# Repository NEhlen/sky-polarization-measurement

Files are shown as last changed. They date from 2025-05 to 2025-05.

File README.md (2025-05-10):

# Sky Polarization Measurement

## Idea
Use four photodiodes with linear polarization filters attached on top with 0°, 45°, 90°, 135° rotation respectively.

From the relative intensities of the measured illumination it is then possible to determine the polarization direction and strength of a light source.

Adding a long tube as a "collimator" along the surface normal of the photodiodes will enable to sample small patches of the sky.

Combining this setup with a 9dof sensor-fusion IMU recording the alt-az and rotation of the tube it is then possible to sway the tube around and continuously record polarization strength/direction to sample the whole sky.

This can be compared to the [Rayleigh sky polarization model](https://en.wikipedia.org/wiki/Rayleigh_sky_model).

## Description
This project uses an ESP32 microcontroller and four BPW34 photodiodes to measure the polarization of the sky. The ESP32 runs a local Wi-Fi access point and serves a JSON API of real-time light intensity values. The analog signals are read using a transimpedance amplifier (TIA) configuration with LM324 op-amps.

## Hardware
### Components
* Espressif ESP32 development board (1x)
* BPW 34 photodiodes (OSRAM) (4x)
* LM 324 Transimpedance amplifier
* GY-9250 9Axis IMU / Adafruit ICM-20948 9-DoF
* Feedback resistors (100&nbsp;kΩ - 1&nbsp;MΩ) (4x)

### Wiring

#### BPW34 / LM324
Each BPW34 photodiode is reverse-biased in a TIA circuit:

* Photodiode anode → GND

* Photodiode cathode → inverting input of LM324

* LM324 non-inverting input → GND

* Feedback resistor between op-amp output and inverting input

* LM324 output → ESP32 analog input (GPIO32, 33, 34, 35)

The LM324 has four op-amps in one package, so one IC is sufficient for all four photodiodes. This is a valid and efficient setup, provided each channel is correctly biased and isolated.

LM324 is powered with 5V (from USB or VIN pin of ESP32).

#### ICM-20948

The ICM-20948 is a 9-axis IMU that combines a 3-axis gyroscope, a 3-axis accelerometer, and a 3-axis magnetometer. Connect it to the ESP32 using the I²C interface as follows:

* **ICM-20948 VCC** → **ESP32 3.3V**
* **ICM-20948 GND** → **ESP32 GND**
* **ICM-20948 SDA** → **ESP32 GPIO21**
* **ICM-20948 SCL** → **ESP32 GPIO22**

Ensure pull-up resistors (typically 4.7kΩ) are present on the SDA and SCL lines if not already included on the breakout board.

#### Breadboard Sketch

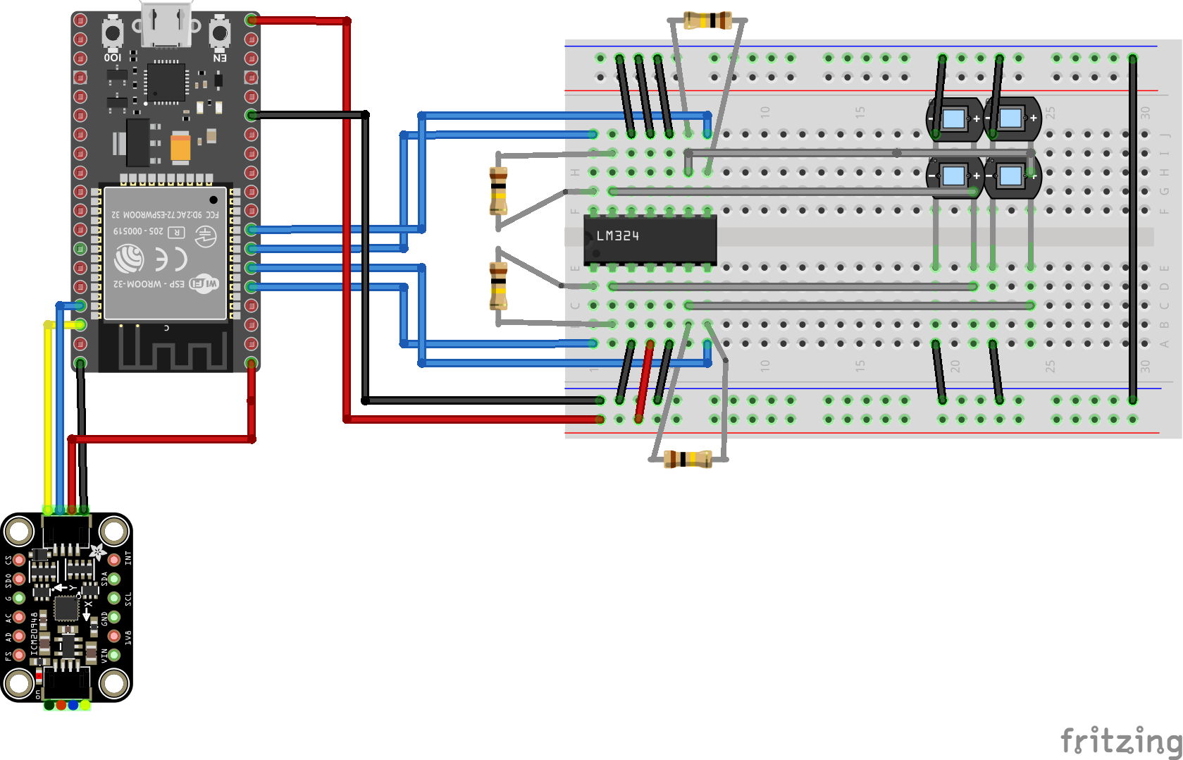
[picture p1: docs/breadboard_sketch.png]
Diode Readout Breadboard Sketch


### Polarizer Setup

Mount the polarizers in front of the photodiodes at 0°, 45°, 90°, and 135° to analyze linear polarization components.

#### BPW 34
The photodiodes are encased in a plastic housing, they are sensitive to vis and near-ir light. The cathode side is marked by a small protrusion on its pin.
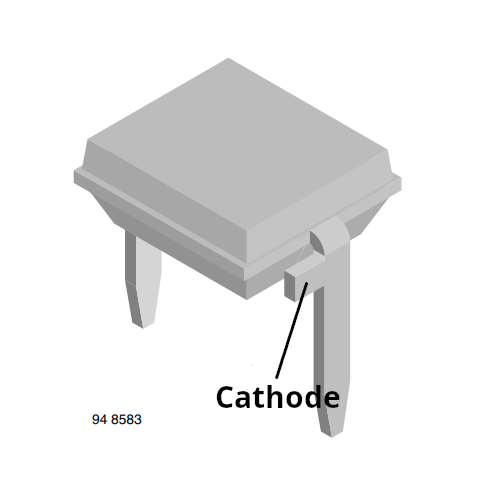
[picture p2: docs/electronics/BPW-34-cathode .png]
Cathode marker


In broad daylight, a voltage of about $0.5-1\,\mathrm{V}$ is produced by a single photodiode. To increase sensitivity and reaction time, the Photodiodes are used in **photoconductive mode** in combination with an LM 324 op-amp rather than **photovoltaic mode** (zero-bias).

#### ICM-20948

The ICM-20948 requires proper initialization in the firmware to read sensor data. Libraries such as [Adafruit's ICM-20948 library](https://github.com/adafruit/Adafruit_ICM20948) can simplify communication and data processing. However, the Adafruit ICM-20948 library **does not give low level access to the digital motion processor (DMP)** on the ICM-20948.
Instead, use the [SparkFun ICM-20948 Arduino Library](https://github.com/sparkfun/SparkFun_ICM-20948_ArduinoLibrary).

The DMP offers a `INV_ICM20948_SENSOR_ORIENTATION` mode that enables access to the 32-bit 9-axis quaternion + heading accuracy without needing to do any additional sensor fusion on the firmware side. From the quaternion, the Euler angles for `yaw`, `tilt` and `roll` can be calculated in the usual manner. This gives alt-az and roll.

## Firmware (ESP32)
The ESP32 sets up a local Wi-Fi Access Point and serves light intensity values as well as alt-az-rot of the ICM-20948 via HTTP at http://192.168.4.1/.

See the firmware at `scripts/esp32/esp32-photodiode-readout-server.ino`

### Serial Plotting
The firmware also prints raw sensor values over serial (space-separated) so you can use the Arduino Serial Plotter for real-time visualization.
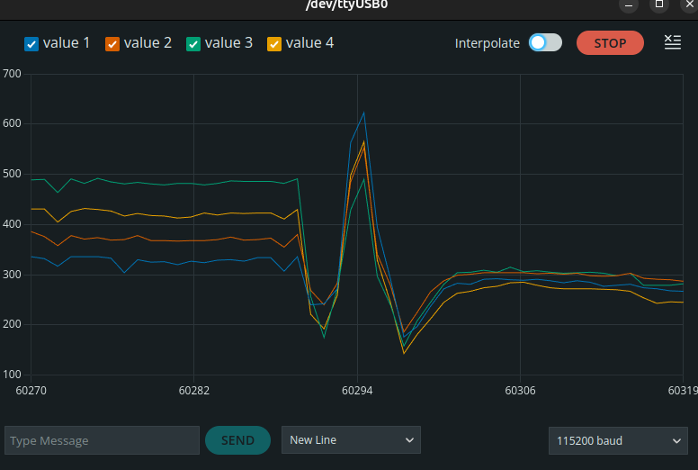
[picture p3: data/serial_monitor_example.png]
Serial Plotting Example


## Calculation of Polarization Direction and Strength

### Simple calculation
With intensities measured through linear polarizers at 0°, 45°, 90°, and 135°, you can compute the Degree of Linear Polarization (DoLP) and Angle of Linear Polarization (AoLP) as follows:

Let:

* $I_0$ = intensity at 0°
* $I_{\pi/4}$ = intensity at 45°
* $I_{\pi/2}$ = intensity at 90°
* $I_{3\pi/4}$ = intensity at 135°

assuming calibrated intensities between all four photodiodes, finding the degree of linear polarization $|P|$ and the angle of polarization $\varphi$ is possible via

```math
\begin{align}
|P| &= \frac{\sqrt{(I_0 - I_{\pi/2})^2 + (I_{\pi/4} - I_{3\pi/4})^2}}{I_0 + I_{\pi/2}}\\
\varphi &= \frac{1}{2} \arctan(I_{\pi/4} - I_{3\pi/4}, I_0 - I_{\pi/2})
\end{align}
```
It may be necessary to calibrate offsets and normalize intensities.

### Optional Fitting

To counter systematic errors and maybe small alignment errors witht he polarization filter, the angle and degree of linear polarization can also be determined by a cosine-fit

```math
\begin{equation}
I(\theta) = I_{\rm unpol} + I_{\rm pol} \cos^2\left(\theta - \theta_{\rm pol}\right)
\end{equation}
```

this formula can be fitted directly by a **nonlinear fitting procedure** netting
```math
\begin{align}
|P| &= \frac{I_{\rm pol}}{I_{\rm unpol} + I_{\rm pol}}\\
\varphi &= \theta_{\rm pol}
\end{align}
```

It would also be possible to do a **linear fitting procedure** by using 
```math
\begin{align}
\cos^2(\theta-\phi) &= \frac{1}{2} \left[1 + \cos(2(\theta - \varphi))\right]\\
\Rightarrow I(\theta) &= C + D \cos(2(\theta - \varphi))
\end{align}
```
with $C= I_{\rm unpol} + 0.5 I_{\rm pol}$ and $D = 0.5 I_{\rm pol}$.

In this case, $\varphi$ is still the polarization angle, but $|P|$ needs to be calculated with

```math
\begin{equation}
|P| = \frac{2D}{2C-D}
\end{equation}
```

## Notes
* Use higher feedback resistance for low-light sensitivity (100kΩ–1MΩ).
* For full ADC range on ESP32 (0–3.3V), adjust gain accordingly.
* The LM324 is not rail-to-rail, but works acceptably in this setup.
* Power the LM324 from the ESP32's VIN (5V from USB).

## Photos

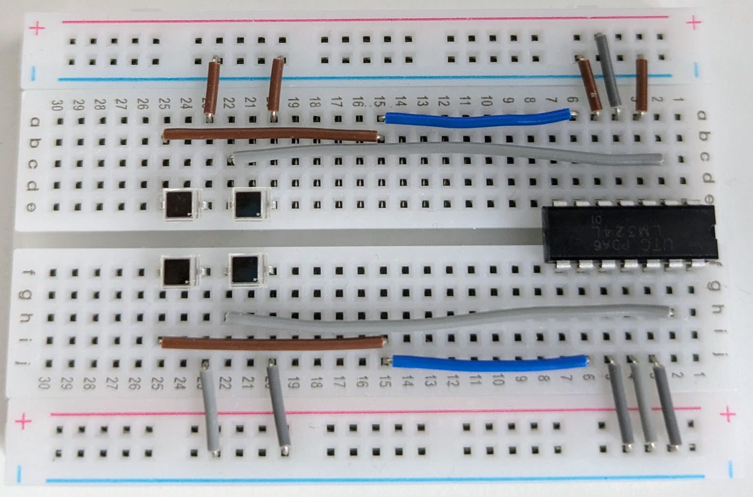
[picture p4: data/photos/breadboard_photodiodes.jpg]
Photodiode placement on breadboard
  
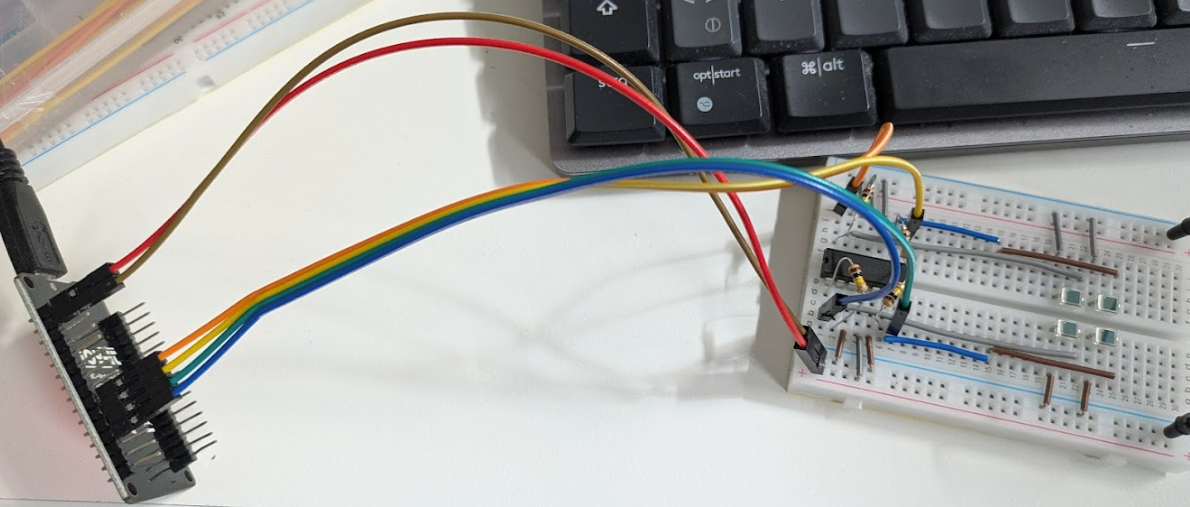
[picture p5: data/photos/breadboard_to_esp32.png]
ESP32 connections


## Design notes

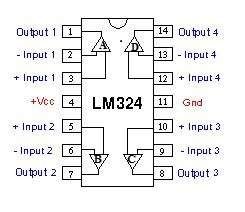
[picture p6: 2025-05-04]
docs/electronics/LM-324-pin-diagram.png

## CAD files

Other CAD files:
data/3d_models/diode_mount.stl

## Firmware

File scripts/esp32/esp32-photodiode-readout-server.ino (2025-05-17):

#include <WiFi.h>
#include <WebServer.h>
#include <ICM_20948.h>

// WiFi credentials for ESP32 AP mode
const char* ssid = "PhotodiodeESP32";
const char* password = "12345678";

// Analog sensor pins
const int sensorPins[4] = {32, 33, 34, 35};
WebServer server(80);

// I2C address configuration for the IMU
#define AD0_VAL 1
ICM_20948_I2C myICM;

// Logging settings
constexpr size_t MAX_SAMPLES = 2400;  // ~4 minutes @ 10Hz
bool loggingEnabled = false;
size_t currentIndex = 0;

// Data structure for each logged sample
struct Sample {
  float alt, az, rot, acc;     // Orientation data
  int16_t s0, s1, s2, s3;       // Averaged sensor values
};
Sample logBuffer[MAX_SAMPLES];

// Buffers for accumulating sensor data between samples
float sensorSum[4] = {0};
int sensorCount = 0;

unsigned long lastSampleTime = 0;

// HTTP endpoint: default help text
void handleRoot() {
  String html = R"rawliteral(
    <!DOCTYPE html>
    <html>
    <head><meta charset='utf-8'><title>ESP32 Logger</title></head>
    <body>
      <h2>ESP32 Datalogger</h2>
      <p>Status: <span id="status">Stopped</span></p>
      <p>Logged Samples: <span id="sampleCount">0</span> / <span id="totalSamples">2000</span></p>
      <button onclick="fetch('/start').then(updateStatus)">Start Logging</button>
      <button onclick="fetch('/stop').then(updateStatus)">Stop Logging</button>
      <br><br>
      <a href="/log.csv" download><button>Download CSV</button></a>

      <script>
        function updateStatus() {
          fetch('/status')
            .then(res => res.json())
            .then(data => {
              document.getElementById('status').textContent = data.logging ? 'Logging' : 'Stopped';
              document.getElementById('sampleCount').textContent = data.samples;
            });
        }
        setInterval(updateStatus, 1000);
        updateStatus();
      </script>
    </body>
    </html>
  )rawliteral";
  server.send(200, "text/html", html);
}

// HTTP endpoint: start logging
void handleStart() {
  loggingEnabled = true;
  currentIndex = 0;
  myICM.resetFIFO();
  memset(sensorSum, 0, sizeof(sensorSum));
  sensorCount = 0;
  server.send(200, "text/plain", "Logging started");
}

// HTTP endpoint: stop logging
void handleStop() {
  loggingEnabled = false;
  server.send(200, "text/plain", "Logging stopped");
}

// HTTP endpoint: return collected log as CSV
void handleCSV() {
  server.setContentLength(CONTENT_LENGTH_UNKNOWN);
  server.send(200, "text/csv", "");
  server.sendContent("alt,az,rot,acc,s0,s1,s2,s3\n");
  for (size_t i = 0; i < currentIndex; ++i) {
    char line[128];
    snprintf(line, sizeof(line), "%.3f,%.3f,%.3f,%.3f,%d,%d,%d,%d\n",
             logBuffer[i].alt, logBuffer[i].az, logBuffer[i].rot, logBuffer[i].acc,
             logBuffer[i].s0, logBuffer[i].s1, logBuffer[i].s2, logBuffer[i].s3);
    server.sendContent(line);
  }
}

void setup() {
  Serial.begin(115200);

  WiFi.softAP(ssid, password);
  delay(100);
  Serial.print("Access Point IP: ");
  Serial.println(WiFi.softAPIP());

  server.on("/", handleRoot);
  server.on("/start", handleStart);
  server.on("/stop", handleStop);
  server.on("/log.csv", handleCSV);
  server.on("/status", []() {
    String json = "{";
    json += "\"logging\":" + String(loggingEnabled ? "true" : "false") + ",";
    json += "\"samples\":" + String(currentIndex);
    json += "}";
    server.send(200, "application/json", json);
  });
  server.begin();

  Wire.begin(21, 22);
  Wire.setClock(400000);

  bool initialized = false;
  while (!initialized) {
    myICM.begin(Wire, AD0_VAL);
    Serial.print(F("Initialization of the sensor returned: "));
    Serial.println(myICM.statusString());
    if (myICM.status != ICM_20948_Stat_Ok) {
      delay(500);
    } else {
      initialized = true;
    }
  }

  bool success = true;
  success &= (myICM.initializeDMP() == ICM_20948_Stat_Ok);
  success &= (myICM.enableDMPSensor(INV_ICM20948_SENSOR_ORIENTATION) == ICM_20948_Stat_Ok);
  success &= (myICM.setDMPODRrate(DMP_ODR_Reg_Quat9, 2) == ICM_20948_Stat_Ok);
  success &= (myICM.enableFIFO() == ICM_20948_Stat_Ok);
  success &= (myICM.enableDMP() == ICM_20948_Stat_Ok);
  success &= (myICM.resetDMP() == ICM_20948_Stat_Ok);
  success &= (myICM.resetFIFO() == ICM_20948_Stat_Ok);

  if (success) Serial.println("DMP enabled");
  else Serial.println("DMP init failed");
}

void loop() {
  unsigned long now = millis();

  // Always accumulate analog sensor values
  for (int i = 0; i < 4; i++) {
    sensorSum[i] += analogRead(sensorPins[i]);
  }
  sensorCount++;

  if (now - lastSampleTime >= 100) {
    lastSampleTime = now;

    if (loggingEnabled && currentIndex < MAX_SAMPLES) {
      // Compute averaged sensor values
      int averagedVals[4];
      for (int i = 0; i < 4; i++) {
        averagedVals[i] = round(sensorSum[i] / sensorCount);
        sensorSum[i] = 0;
      }
      sensorCount = 0;

      float alt = 0, az = 0, rot = 0, acc = 0;
      bool imuDataValid = false;

      icm_20948_DMP_data_t data;
      myICM.readDMPdataFromFIFO(&data);

      if ((myICM.status == ICM_20948_Stat_Ok || myICM.status == ICM_20948_Stat_FIFOMoreDataAvail)
          && (data.header & DMP_header_bitmap_Quat9)) {
        double q1 = ((double)data.Quat9.Data.Q1) / 1073741824.0;
        double q2 = ((double)data.Quat9.Data.Q2) / 1073741824.0;
        double q3 = ((double)data.Quat9.Data.Q3) / 1073741824.0;
        double q_squared_sum = q1*q1 + q2*q2 + q3*q3;
        double q0 = 0;
        if (q_squared_sum <= 1.0) {
          q0 = sqrt(1.0 - q_squared_sum);
          az   = atan2(2.0 * (q0*q3 + q1*q2), 1.0 - 2.0 * (q2*q2 + q3*q3)) * 180.0 / PI;
          alt  = asin(2.0 * (q0*q2 - q3*q1)) * 180.0 / PI;
          rot  = atan2(2.0 * (q0*q1 + q2*q3), 1.0 - 2.0 * (q1*q1 + q2*q2)) * 180.0 / PI;
          if (az < 0) az += 360.0;
          acc = data.Quat9.Data.Accuracy;
          imuDataValid = true;
        }
      }

      // Store sample only if valid IMU data was read
      if (imuDataValid) {
        logBuffer[currentIndex++] = {
          alt, az, rot, acc,
          (int16_t)averagedVals[0], (int16_t)averagedVals[1],
          (int16_t)averagedVals[2], (int16_t)averagedVals[3]
        };
      }
    }
  }

  server.handleClient();
}

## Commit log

2025-05-10 added 9dof imu documentation
    [sketch.fzz]
2025-05-17 track .blend and .stl with LFS
    [diode_mount.blend, diode_mount.stl]
